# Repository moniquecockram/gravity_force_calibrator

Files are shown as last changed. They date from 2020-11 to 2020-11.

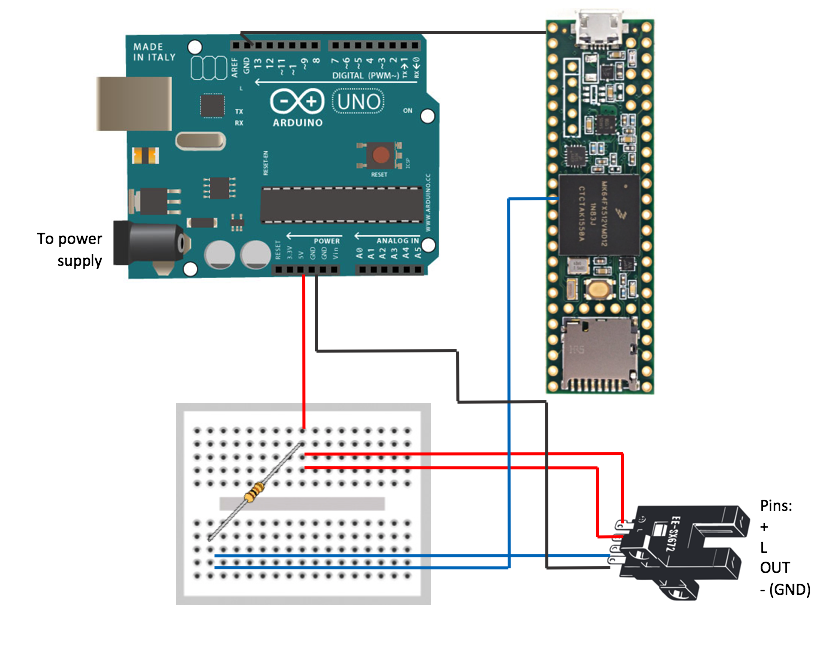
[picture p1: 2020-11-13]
Part Images/wiring_diagram.png

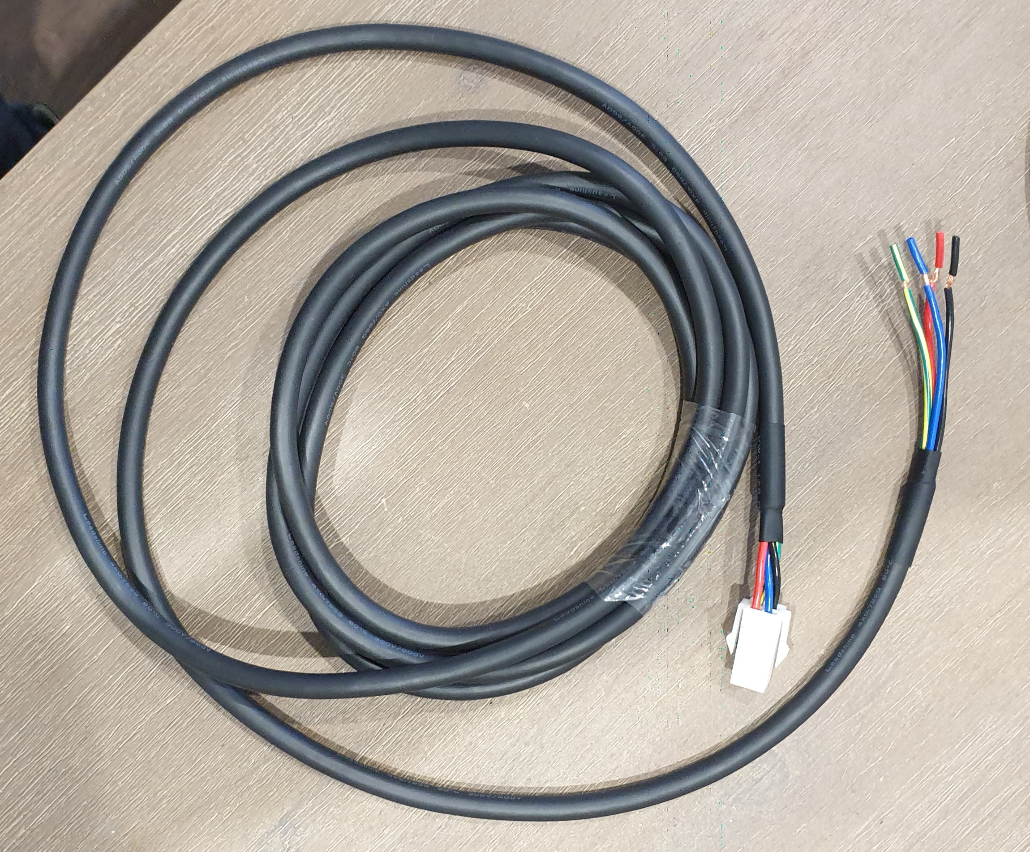
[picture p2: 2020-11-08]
Part Images/Metre Power Extension Cable for Easy Servo Motors_1.jpg

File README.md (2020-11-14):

# gravity_force_calibrator
A wheely good project.

The current version of the code to run the prototype is in folder control_code. 

The simple code for reading photogate data is in photogate_MArk1.

Other useful information on the various aspects of the project are in other folders as labelled.

Ryan Husband and Monique Cockram

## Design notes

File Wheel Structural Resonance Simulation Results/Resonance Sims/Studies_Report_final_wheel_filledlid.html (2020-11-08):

Image Width (pixels):

# Study Report

Analyzed File | better_combined_filledlid v9
Version | Autodesk Fusion 360 (2.0.8809)
Creation Date | 2020-08-21, 23:20:54
Author | ryanh

#### Project Properties

Title | Studies
Author | ryanh

## Simulation Model 1:1

### Study 1 - Modal Frequencies

##### Study Properties

Study Type | Modal Frequencies
Last Modification Date | 2020-08-21, 21:56:54

#### Settings

##### General

Contact Tolerance | 0.1 mm
Number of Modes | 10
Frequency Range [Hz] | No
Compute Preloaded Modes | Yes
Enhanced Accuracy | No

##### Damping

##### Mesh

Average Element Size (% of model size)
Solids | 3
Scale Mesh Size Per Part | No
Average Element Size (absolute value) | -
Element Order | Parabolic
Create Curved Mesh Elements | Yes
Max. Turn Angle on Curves (Deg.) | 60
Max. Adjacent Mesh Size Ratio | 1.5
Max. Aspect Ratio | 10
Minimum Element Size (% of average size) | 20

##### Adaptive Mesh Refinement

Number of Refinement Steps | 0
Results Convergence Tolerance (%) | 20
Frequency Mode | 1

#### Materials

Component | Material | Safety Factor
Body1 | Aluminum | Yield Strength
Body3 | Aluminum | Yield Strength
better_combined_innerlid v13:1 | Aluminum | Yield Strength
better_combined_innerlid v13:1/weight_lids v2:1 | Aluminum | Yield Strength
better_combined_innerlid v13:1/weight_lids v2:2 | Aluminum | Yield Strength
better_combined_innerlid v13:1/better_combined v19:1/axel v5:1 | Aluminum | Yield Strength
better_combined_innerlid v13:1/better_combined v19:1/design_MArk2 v17:1 | Aluminum | Yield Strength
better_combined_innerlid v13:1/better_combined v19:1/weights v2:1 | Steel | Yield Strength
better_combined_innerlid v13:1/better_combined v19:1/weights v2:2 | Steel | Yield Strength
better_combined_innerlid v13:1/better_combined v19:1/holders v12:1 | Aluminum | Yield Strength
better_combined_innerlid v13:1/better_combined v19:1/holders v12:2 | Aluminum | Yield Strength

##### Aluminum

Density | 2.7E-06 kg / mm^3
Young's Modulus | 68900 MPa
Poisson's Ratio | 0.33
Yield Strength | 275 MPa
Ultimate Tensile Strength | 310 MPa
Thermal Conductivity | 0.23 W / (mm C)
Thermal Expansion Coefficient | 2.36E-05 / C
Specific Heat | 897 J / (kg C)

##### Steel

Density | 7.85E-06 kg / mm^3
Young's Modulus | 210000 MPa
Poisson's Ratio | 0.3
Yield Strength | 207 MPa
Ultimate Tensile Strength | 345 MPa
Thermal Conductivity | 0.056 W / (mm C)
Thermal Expansion Coefficient | 1.2E-05 / C
Specific Heat | 480 J / (kg C)

#### Contacts

##### Bonded

Name

[S] Bonded1 [weights v2:2||holders v12:2]

[S] Bonded2 [weights v2:1||holders v12:1]

[S] Bonded3 [design_MArk2 v17:1||weights v2:1]

[S] Bonded4 [design_MArk2 v17:1||holders v12:1]

[S] Bonded5 [design_MArk2 v17:1||holders v12:1]

[S] Bonded6 [design_MArk2 v17:1||holders v12:1]

[S] Bonded7 [design_MArk2 v17:1||weights v2:1]

[S] Bonded8 [design_MArk2 v17:1||weights v2:1]

[S] Bonded9 [design_MArk2 v17:1||weights v2:2]

[S] Bonded10 [design_MArk2 v17:1||holders v12:2]

[S] Bonded11 [design_MArk2 v17:1||holders v12:2]

[S] Bonded12 [design_MArk2 v17:1||weights v2:2]

[S] Bonded13 [design_MArk2 v17:1||weights v2:2]

[S] Bonded14 [design_MArk2 v17:1||holders v12:1]

[S] Bonded15 [design_MArk2 v17:1||holders v12:1]

[S] Bonded16 [design_MArk2 v17:1||weights v2:1]

[S] Bonded17 [design_MArk2 v17:1||holders v12:2]

[S] Bonded18 [design_MArk2 v17:1||holders v12:2]

[S] Bonded19 [design_MArk2 v17:1||weights v2:2]

[S] Bonded20 [design_MArk2 v17:1||weights v2:1]

[S] Bonded21 [design_MArk2 v17:1||holders v12:2]

[S] Bonded22 [design_MArk2 v17:1||weights v2:2]

[S] Bonded23 [axel v5:1||design_MArk2 v17:1]

[S] Bonded24 [weight_lids v2:2||holders v12:1]

[S] Bonded25 [weight_lids v2:2||weights v2:1]

[S] Bonded26 [weight_lids v2:2||design_MArk2 v17:1]

[S] Bonded27 [weight_lids v2:1||holders v12:2]

[S] Bonded28 [weight_lids v2:1||weights v2:2]

[S] Bonded29 [weight_lids v2:1||design_MArk2 v17:1]

[S] Bonded30 [better_combined_innerlid v13:1||weight_lids v2:2]

[S] Bonded31 [better_combined_innerlid v13:1||weight_lids v2:1]

[S] Bonded32 [better_combined_innerlid v13:1||design_MArk2 v17:1]

[S] Bonded33 [better_combined_innerlid v13:1||design_MArk2 v17:1]

[S] Bonded34 [better_combined_innerlid v13:1||design_MArk2 v17:1]

[S] Bonded35 [better_combined_innerlid v13:1||design_MArk2 v17:1]

[S] Bonded36 [better_combined_innerlid v13:1||design_MArk2 v17:1]

[S] Bonded37 [better_combined_innerlid v13:1||design_MArk2 v17:1]

[S] Bonded38 [better_combined_innerlid v13:1||design_MArk2 v17:1]

[S] Bonded39 [better_combined_innerlid v13:1||design_MArk2 v17:1]

[S] Bonded40 [better_combined_innerlid v13:1||weights v2:1]

[S] Bonded41 [better_combined_innerlid v13:1||holders v12:1]

[S] Bonded42 [better_combined_innerlid v13:1||holders v12:1]

[S] Bonded43 [better_combined_innerlid v13:1||holders v12:1]

[S] Bonded44 [better_combined_innerlid v13:1||weights v2:1]

[S] Bonded45 [better_combined_innerlid v13:1||weights v2:1]

[S] Bonded46 [better_combined_innerlid v13:1||weights v2:2]

[S] Bonded47 [better_combined_innerlid v13:1||holders v12:2]

[S] Bonded48 [better_combined_innerlid v13:1||holders v12:2]

[S] Bonded49 [better_combined_innerlid v13:1||weights v2:2]

[S] Bonded50 [better_combined_innerlid v13:1||weights v2:2]

[S] Bonded51 [better_combined_innerlid v13:1||holders v12:1]

[S] Bonded52 [better_combined_innerlid v13:1||holders v12:1]

[S] Bonded53 [better_combined_innerlid v13:1||weights v2:1]

[S] Bonded54 [better_combined_innerlid v13:1||holders v12:2]

[S] Bonded55 [better_combined_innerlid v13:1||holders v12:2]

[S] Bonded56 [better_combined_innerlid v13:1||weights v2:2]

[S] Bonded57 [better_combined_innerlid v13:1||weights v2:1]

[S] Bonded58 [better_combined_innerlid v13:1||holders v12:2]

[S] Bonded59 [better_combined_innerlid v13:1||weights v2:2]

[S] Bonded60 [better_combined_innerlid v13:1||axel v5:1]

[S] Bonded61 [Simulation Model 1:1(Body3)||design_MArk2 v17:1]

[S] Bonded62 [Simulation Model 1:1(Body3)||better_combined_innerlid v13:1]

[S] Bonded63 [Simulation Model 1:1(Body3)||better_combined_innerlid v13:1]

[S] Bonded64 [Simulation Model 1:1(Body3)||design_MArk2 v17:1]

[S] Bonded65 [Simulation Model 1:1(Body3)||better_combined_innerlid v13:1]

[S] Bonded66 [Simulation Model 1:1(Body3)||better_combined_innerlid v13:1]

[S] Bonded67 [Simulation Model 1:1(Body1)||design_MArk2 v17:1]

[S] Bonded68 [Simulation Model 1:1(Body1)||better_combined_innerlid v13:1]

[S] Bonded69 [Simulation Model 1:1(Body1)||better_combined_innerlid v13:1]

[S] Bonded70 [Simulation Model 1:1(Body1)||design_MArk2 v17:1]

[S] Bonded71 [Simulation Model 1:1(Body1)||better_combined_innerlid v13:1]

[S] Bonded72 [Simulation Model 1:1(Body1)||better_combined_innerlid v13:1]

#### Mesh

Type | Nodes | Elements
Solids | 476671 | 314592

#### Load Case1

#### Constraints

##### Frictionless1

Type | Frictionless

###### Selected Entities

For correct interpretation of this image use e.g. IE9, Chrome, Safari, Firefox

##### Pin1

Type | Pin
Radial | Yes
Axial | Yes
Tangential | No

###### Selected Entities

For correct interpretation of this image use e.g. IE9, Chrome, Safari, Firefox

##### Pin2

Type | Pin
Radial | Yes
Axial | Yes
Tangential | No

###### Selected Entities

For correct interpretation of this image use e.g. IE9, Chrome, Safari, Firefox

#### Loads

##### Gravity

Type | Gravity
Magnitude | 9.807 m / s^2
X Value | 0 m / s^2
Y Value | 0 m / s^2
Z Value | -9.807 m / s^2

###### Selected Entities

For correct interpretation of this image use e.g. IE9, Chrome, Safari, Firefox

##### Angular Global Load1

Type | Angular Global Load
Velocity
Magnitude | 360 deg / s
X Value | 0 deg / s
Y Value | 0 deg / s
Z Value | -360 deg / s
X Distance | 0 mm
Y Distance | 0 mm
Z Distance | 0 mm

###### Selected Entities

For correct interpretation of this image use e.g. IE9, Chrome, Safari, Firefox

#### Results

##### Result Summary

Frequency | Participation X | Participation Y | Participation Z
Mode 1: 117.6 Hz | 0 | 0 | 0
Mode 2: 1059 Hz | 0.0015 | 0 | 0
Mode 3: 1109 Hz | 0 | 0.0002 | 0
Mode 4: 1588 Hz | 0 | 0 | 84.2124999
Mode 5: 2258 Hz | 0 | 0.0002 | 1.19500002
Mode 6: 2334 Hz | 0 | 0 | 0.0005
Mode 7: 2814 Hz | 0.0012 | 89.0425026 | 0
Mode 8: 3084 Hz | 89.5721018 | 0.001 | 0
Mode 9: 4229 Hz | 0 | 0.0005 | 0.0003
Mode 10: 4243 Hz | 0 | 0 | 0.239500008

##### Total Modal Displacement

###### Mode 1: 117.6 Hz Total Modal Displacement

0 1

For correct interpretation of this image use e.g. IE9, Chrome, Safari, Firefox

###### Mode 2: 1059 Hz Total Modal Displacement

0 1

For correct interpretation of this image use e.g. IE9, Chrome, Safari, Firefox

###### Mode 3: 1109 Hz Total Modal Displacement

0 1

For correct interpretation of this image use e.g. IE9, Chrome, Safari, Firefox

###### Mode 4: 1588 Hz Total Modal Displacement

0 1

For correct interpretation of this image use e.g. IE9, Chrome, Safari, Firefox

###### Mode 5: 2258 Hz Total Modal Displacement

0 1

For correct interpretation of this image use e.g. IE9, Chrome, Safari, Firefox

###### Mode 6: 2334 Hz Total Modal Displacement

0 1

For correct interpretation of this image use e.g. IE9, Chrome, Safari, Firefox

###### Mode 7: 2814 Hz Total Modal Displacement

0 1

For correct interpretation of this image use e.g. IE9, Chrome, Safari, Firefox

###### Mode 8: 3084 Hz Total Modal Displacement

0 1

For correct interpretation of this image use e.g. IE9, Chrome, Safari, Firefox

###### Mode 9: 4229 Hz Total Modal Displacement

0 1

For correct interpretation of this image use e.g. IE9, Chrome, Safari, Firefox

###### Mode 10: 4243 Hz Total Modal Displacement

0 1

For correct interpretation of this image use e.g. IE9, Chrome, Safari, Firefox

Image Width (pixels):

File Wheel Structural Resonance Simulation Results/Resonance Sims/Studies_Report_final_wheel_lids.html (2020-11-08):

Image Width (pixels):

# Study Report

Analyzed File | better_combined_outerlids v5
Version | Autodesk Fusion 360 (2.0.8809)
Creation Date | 2020-08-21, 18:55:14
Author | ryanh

#### Project Properties

Title | Studies
Author | ryanh

## Simulation Model 1:1

### Study 1 - Modal Frequencies

##### Study Properties

Study Type | Modal Frequencies
Last Modification Date | 2020-08-21, 17:08:25

#### Settings

##### General

Contact Tolerance | 0.1 mm
Number of Modes | 10
Frequency Range [Hz] | No
Compute Preloaded Modes | Yes
Enhanced Accuracy | No

##### Damping

##### Mesh

Average Element Size (% of model size)
Solids | 3
Scale Mesh Size Per Part | No
Average Element Size (absolute value) | -
Element Order | Parabolic
Create Curved Mesh Elements | Yes
Max. Turn Angle on Curves (Deg.) | 60
Max. Adjacent Mesh Size Ratio | 1.5
Max. Aspect Ratio | 10
Minimum Element Size (% of average size) | 20

##### Adaptive Mesh Refinement

Number of Refinement Steps | 0
Results Convergence Tolerance (%) | 20
Frequency Mode | 1

#### Materials

Component | Material | Safety Factor
better_combined v17:1/axel v5:1 | Aluminum | Yield Strength
better_combined v17:1/design_MArk2 v17:1 | Aluminum | Yield Strength
better_combined v17:1/weights v2:1 | Steel | Yield Strength
better_combined v17:1/weights v2:2 | Steel | Yield Strength
better_combined v17:1/holders v12:1 | Aluminum | Yield Strength
better_combined v17:1/holders v12:2 | Aluminum | Yield Strength
lid v4:1 | Aluminum | Yield Strength
lid v4:2 | Aluminum | Yield Strength

##### Aluminum

Density | 2.7E-06 kg / mm^3
Young's Modulus | 68900 MPa
Poisson's Ratio | 0.33
Yield Strength | 275 MPa
Ultimate Tensile Strength | 310 MPa
Thermal Conductivity | 0.23 W / (mm C)
Thermal Expansion Coefficient | 2.36E-05 / C
Specific Heat | 897 J / (kg C)

##### Steel

Density | 7.85E-06 kg / mm^3
Young's Modulus | 210000 MPa
Poisson's Ratio | 0.3
Yield Strength | 207 MPa
Ultimate Tensile Strength | 345 MPa
Thermal Conductivity | 0.056 W / (mm C)
Thermal Expansion Coefficient | 1.2E-05 / C
Specific Heat | 480 J / (kg C)

#### Contacts

##### Bonded

Name

[M] [S] Bonded1 [lid v4:1||design_MArk2 v17:1]

[M] [S] Bonded2 [lid v4:2||design_MArk2 v17:1]

[M] [S] Bonded3 [weights v2:1||design_MArk2 v17:1]

[M] [S] Bonded4 [weights v2:2||design_MArk2 v17:1]

[M] [S] Bonded5 [holders v12:2||design_MArk2 v17:1]

[M] [S] Bonded6 [holders v12:1||design_MArk2 v17:1]

[M] [S] Bonded7 [lid v4:1||axel v5:1]

[M] [S] Bonded8 [lid v4:2||axel v5:1]

[S] Bonded9 [holders v12:2||lid v4:1]

[S] Bonded10 [holders v12:1||lid v4:1]

[S] Bonded11 [weights v2:2||lid v4:1]

[S] Bonded12 [weights v2:2||holders v12:2]

[S] Bonded13 [weights v2:1||lid v4:1]

[S] Bonded14 [weights v2:1||holders v12:1]

[S] Bonded15 [design_MArk2 v17:1||weights v2:1]

[S] Bonded16 [design_MArk2 v17:1||holders v12:1]

[S] Bonded17 [design_MArk2 v17:1||holders v12:1]

[S] Bonded18 [design_MArk2 v17:1||weights v2:1]

[S] Bonded19 [design_MArk2 v17:1||weights v2:1]

[S] Bonded20 [design_MArk2 v17:1||weights v2:2]

[S] Bonded21 [design_MArk2 v17:1||holders v12:2]

[S] Bonded22 [design_MArk2 v17:1||holders v12:2]

[S] Bonded23 [design_MArk2 v17:1||weights v2:2]

[S] Bonded24 [design_MArk2 v17:1||weights v2:2]

[S] Bonded25 [design_MArk2 v17:1||holders v12:1]

[S] Bonded26 [design_MArk2 v17:1||holders v12:1]

[S] Bonded27 [design_MArk2 v17:1||holders v12:2]

[S] Bonded28 [design_MArk2 v17:1||holders v12:2]

[S] Bonded29 [design_MArk2 v17:1||weights v2:1]

[S] Bonded30 [design_MArk2 v17:1||weights v2:2]

[S] Bonded31 [axel v5:1||design_MArk2 v17:1]

#### Mesh

Type | Nodes | Elements
Solids | 655869 | 426144

#### Load Case1

#### Constraints

##### Frictionless1

Type | Frictionless

###### Selected Entities

For correct interpretation of this image use e.g. IE9, Chrome, Safari, Firefox

##### Pin1

Type | Pin
Radial | Yes
Axial | Yes
Tangential | No

###### Selected Entities

For correct interpretation of this image use e.g. IE9, Chrome, Safari, Firefox

##### Pin2

Type | Pin
Radial | Yes
Axial | Yes
Tangential | No

###### Selected Entities

For correct interpretation of this image use e.g. IE9, Chrome, Safari, Firefox

##### Pin3

Type | Pin
Radial | Yes
Axial | Yes
Tangential | No

###### Selected Entities

For correct interpretation of this image use e.g. IE9, Chrome, Safari, Firefox

##### Pin4

Type | Pin
Radial | Yes
Axial | Yes
Tangential | No

###### Selected Entities

For correct interpretation of this image use e.g. IE9, Chrome, Safari, Firefox

#### Loads

##### Gravity

Type | Gravity
Magnitude | 9.807 m / s^2
X Value | 0 m / s^2
Y Value | 0 m / s^2
Z Value | -9.807 m / s^2

###### Selected Entities

For correct interpretation of this image use e.g. IE9, Chrome, Safari, Firefox

##### Angular Global Load1

Type | Angular Global Load
Velocity
Magnitude | 360 deg / s
X Value | 0 deg / s
Y Value | 0 deg / s
Z Value | -360 deg / s
X Distance | 0 mm
Y Distance | 0 mm
Z Distance | 0 mm

###### Selected Entities

For correct interpretation of this image use e.g. IE9, Chrome, Safari, Firefox

#### Results

##### Result Summary

Frequency | Participation X | Participation Y | Participation Z
Mode 1: 61.13 Hz | 0 | 0 | 0
Mode 2: 827.1 Hz | 0 | 0.0065 | 0.0001
Mode 3: 1020 Hz | 0.0043 | 0 | 0.022
Mode 4: 1078 Hz | 0 | 0 | 75.8481026
Mode 5: 1839 Hz | 0 | 84.751302 | 0
Mode 6: 1979 Hz | 0 | 0.0002 | 3.38249989
Mode 7: 2213 Hz | 0 | 0.033099999 | 0
Mode 8: 2217 Hz | 0.0001 | 0.620900001 | 0
Mode 9: 2257 Hz | 0 | 0.0017 | 0.0003
Mode 10: 2311 Hz | 0 | 0 | 1.02129998

##### Total Modal Displacement

###### Mode 1: 61.13 Hz Total Modal Displacement

0.001 1

For correct interpretation of this image use e.g. IE9, Chrome, Safari, Firefox

###### Mode 2: 827.1 Hz Total Modal Displacement

0 1

For correct interpretation of this image use e.g. IE9, Chrome, Safari, Firefox

###### Mode 3: 1020 Hz Total Modal Displacement

0 1

For correct interpretation of this image use e.g. IE9, Chrome, Safari, Firefox

###### Mode 4: 1078 Hz Total Modal Displacement

0 1

For correct interpretation of this image use e.g. IE9, Chrome, Safari, Firefox

###### Mode 5: 1839 Hz Total Modal Displacement

0 1

For correct interpretation of this image use e.g. IE9, Chrome, Safari, Firefox

###### Mode 6: 1979 Hz Total Modal Displacement

0 1

For correct interpretation of this image use e.g. IE9, Chrome, Safari, Firefox

###### Mode 7: 2213 Hz Total Modal Displacement

0 1

For correct interpretation of this image use e.g. IE9, Chrome, Safari, Firefox

###### Mode 8: 2217 Hz Total Modal Displacement

0 1

For correct interpretation of this image use e.g. IE9, Chrome, Safari, Firefox

###### Mode 9: 2257 Hz Total Modal Displacement

0 1

For correct interpretation of this image use e.g. IE9, Chrome, Safari, Firefox

###### Mode 10: 2311 Hz Total Modal Displacement

0 1

For correct interpretation of this image use e.g. IE9, Chrome, Safari, Firefox

Image Width (pixels):

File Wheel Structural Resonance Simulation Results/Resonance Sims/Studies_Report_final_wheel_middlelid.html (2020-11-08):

Image Width (pixels):

# Study Report

Analyzed File | better_combined_innerlid v11
Version | Autodesk Fusion 360 (2.0.8809)
Creation Date | 2020-08-21, 21:32:29
Author | ryanh

#### Project Properties

Title | Studies
Author | ryanh

## Simulation Model 1:1

### Study 1 - Modal Frequencies

##### Study Properties

Study Type | Modal Frequencies
Last Modification Date | 2020-08-21, 21:18:28

#### Settings

##### General

Contact Tolerance | 0.1 mm
Number of Modes | 10
Frequency Range [Hz] | No
Compute Preloaded Modes | Yes
Enhanced Accuracy | No

##### Damping

##### Mesh

Average Element Size (% of model size)
Solids | 3
Scale Mesh Size Per Part | No
Average Element Size (absolute value) | -
Element Order | Parabolic
Create Curved Mesh Elements | Yes
Max. Turn Angle on Curves (Deg.) | 60
Max. Adjacent Mesh Size Ratio | 1.5
Max. Aspect Ratio | 10
Minimum Element Size (% of average size) | 20

##### Adaptive Mesh Refinement

Number of Refinement Steps | 0
Results Convergence Tolerance (%) | 20
Frequency Mode | 1

#### Materials

Component | Material | Safety Factor
Body1 | Aluminum | Yield Strength
better_combined v18:1/axel v5:1 | Aluminum | Yield Strength
better_combined v18:1/design_MArk2 v17:1 | Aluminum | Yield Strength
better_combined v18:1/weights v2:1 | Steel | Yield Strength
better_combined v18:1/weights v2:2 | Steel | Yield Strength
better_combined v18:1/holders v12:1 | Aluminum | Yield Strength
better_combined v18:1/holders v12:2 | Aluminum | Yield Strength
weight_lids v2:1 | Aluminum | Yield Strength
weight_lids v2:2 | Aluminum | Yield Strength

##### Aluminum

Density | 2.7E-06 kg / mm^3
Young's Modulus | 68900 MPa
Poisson's Ratio | 0.33
Yield Strength | 275 MPa
Ultimate Tensile Strength | 310 MPa
Thermal Conductivity | 0.23 W / (mm C)
Thermal Expansion Coefficient | 2.36E-05 / C
Specific Heat | 897 J / (kg C)

##### Steel

Density | 7.85E-06 kg / mm^3
Young's Modulus | 210000 MPa
Poisson's Ratio | 0.3
Yield Strength | 207 MPa
Ultimate Tensile Strength | 345 MPa
Thermal Conductivity | 0.056 W / (mm C)
Thermal Expansion Coefficient | 1.2E-05 / C
Specific Heat | 480 J / (kg C)

#### Contacts

##### Bonded

Name

[M] [S] Bonded3 [Simulation Model 1:1||]

[M] [S] Bonded4 [||Simulation Model 1:1]

[M] [S] Bonded6 [||Simulation Model 1:1]

[M] [S] Bonded7 [||Simulation Model 1:1]

[S] Bonded61 [holders v12:2||weight_lids v2:1]

[S] Bonded62 [holders v12:1||weight_lids v2:2]

[S] Bonded63 [weights v2:2||weight_lids v2:1]

[S] Bonded64 [weights v2:2||holders v12:2]

[S] Bonded65 [weights v2:1||weight_lids v2:2]

[S] Bonded66 [weights v2:1||holders v12:1]

[S] Bonded67 [design_MArk2 v17:1||weight_lids v2:2]

[S] Bonded68 [design_MArk2 v17:1||weight_lids v2:1]

[S] Bonded69 [design_MArk2 v17:1||weights v2:1]

[S] Bonded70 [design_MArk2 v17:1||holders v12:1]

[S] Bonded71 [design_MArk2 v17:1||holders v12:1]

[S] Bonded72 [design_MArk2 v17:1||holders v12:1]

[S] Bonded73 [design_MArk2 v17:1||weights v2:1]

[S] Bonded74 [design_MArk2 v17:1||weights v2:1]

[S] Bonded75 [design_MArk2 v17:1||weights v2:2]

[S] Bonded76 [design_MArk2 v17:1||holders v12:2]

[S] Bonded77 [design_MArk2 v17:1||holders v12:2]

[S] Bonded78 [design_MArk2 v17:1||weights v2:2]

[S] Bonded79 [design_MArk2 v17:1||weights v2:2]

[S] Bonded80 [design_MArk2 v17:1||holders v12:1]

[S] Bonded81 [design_MArk2 v17:1||holders v12:1]

[S] Bonded82 [design_MArk2 v17:1||weights v2:1]

[S] Bonded83 [design_MArk2 v17:1||holders v12:2]

[S] Bonded84 [design_MArk2 v17:1||holders v12:2]

[S] Bonded85 [design_MArk2 v17:1||weights v2:2]

[S] Bonded86 [design_MArk2 v17:1||weights v2:1]

[S] Bonded87 [design_MArk2 v17:1||holders v12:2]

[S] Bonded88 [design_MArk2 v17:1||weights v2:2]

[S] Bonded89 [axel v5:1||design_MArk2 v17:1]

[S] Bonded90 [Simulation Model 1:1||weight_lids v2:2]

[S] Bonded91 [Simulation Model 1:1||weight_lids v2:1]

[S] Bonded92 [Simulation Model 1:1||design_MArk2 v17:1]

[S] Bonded93 [Simulation Model 1:1||design_MArk2 v17:1]

[S] Bonded94 [Simulation Model 1:1||design_MArk2 v17:1]

[S] Bonded95 [Simulation Model 1:1||design_MArk2 v17:1]

[S] Bonded96 [Simulation Model 1:1||design_MArk2 v17:1]

[S] Bonded97 [Simulation Model 1:1||design_MArk2 v17:1]

[S] Bonded98 [Simulation Model 1:1||design_MArk2 v17:1]

[S] Bonded99 [Simulation Model 1:1||design_MArk2 v17:1]

[S] Bonded100 [Simulation Model 1:1||weights v2:1]

[S] Bonded101 [Simulation Model 1:1||holders v12:1]

[S] Bonded102 [Simulation Model 1:1||holders v12:1]

[S] Bonded103 [Simulation Model 1:1||holders v12:1]

[S] Bonded104 [Simulation Model 1:1||weights v2:1]

[S] Bonded105 [Simulation Model 1:1||weights v2:1]

[S] Bonded106 [Simulation Model 1:1||weights v2:2]

[S] Bonded107 [Simulation Model 1:1||holders v12:2]

[S] Bonded108 [Simulation Model 1:1||holders v12:2]

[S] Bonded109 [Simulation Model 1:1||weights v2:2]

[S] Bonded110 [Simulation Model 1:1||weights v2:2]

[S] Bonded111 [Simulation Model 1:1||holders v12:1]

[S] Bonded112 [Simulation Model 1:1||holders v12:1]

[S] Bonded113 [Simulation Model 1:1||weights v2:1]

[S] Bonded114 [Simulation Model 1:1||holders v12:2]

[S] Bonded115 [Simulation Model 1:1||holders v12:2]

[S] Bonded116 [Simulation Model 1:1||weights v2:2]

[S] Bonded117 [Simulation Model 1:1||weights v2:1]

[S] Bonded118 [Simulation Model 1:1||holders v12:2]

[S] Bonded119 [Simulation Model 1:1||weights v2:2]

[S] Bonded120 [Simulation Model 1:1||axel v5:1]

#### Mesh

Type | Nodes | Elements
Solids | 215918 | 136483

#### Load Case1

#### Constraints

##### Frictionless1

Type | Frictionless

###### Selected Entities

For correct interpretation of this image use e.g. IE9, Chrome, Safari, Firefox

##### Pin1

Type | Pin
Radial | Yes
Axial | Yes
Tangential | No

###### Selected Entities

For correct interpretation of this image use e.g. IE9, Chrome, Safari, Firefox

##### Pin2

Type | Pin
Radial | Yes
Axial | Yes
Tangential | No

###### Selected Entities

For correct interpretation of this image use e.g. IE9, Chrome, Safari, Firefox

#### Loads

##### Gravity

Type | Gravity
Magnitude | 9.807 m / s^2
X Value | 0 m / s^2
Y Value | 0 m / s^2
Z Value | -9.807 m / s^2

###### Selected Entities

For correct interpretation of this image use e.g. IE9, Chrome, Safari, Firefox

##### Angular Global Load1

Type | Angular Global Load
Velocity
Magnitude | 360 deg / s
X Value | 0 deg / s
Y Value | 0 deg / s
Z Value | -360 deg / s
X Distance | 0 mm
Y Distance | 0 mm
Z Distance | 0 mm

###### Selected Entities

For correct interpretation of this image use e.g. IE9, Chrome, Safari, Firefox

#### Results

##### Result Summary

Frequency | Participation X | Participation Y | Participation Z
Mode 1: 132.3 Hz | 0 | 0 | 0
Mode 2: 645 Hz | 0 | 0.0021 | 0
Mode 3: 935.3 Hz | 0 | 0 | 61.7972016
Mode 4: 1024 Hz | 0.0073 | 0 | 0.0005
Mode 5: 1151 Hz | 0 | 0.0088 | 0.0004
Mode 6: 1153 Hz | 0 | 0.0001 | 0.039199999
Mode 7: 1227 Hz | 16.2856996 | 0 | 0
Mode 8: 1256 Hz | 0.0005 | 0 | 0
Mode 9: 1486 Hz | 0 | 65.9582019 | 0
Mode 10: 1513 Hz | 0 | 0 | 15.5499995

##### Total Modal Displacement

###### Mode 1: 132.3 Hz Total Modal Displacement

0 1

For correct interpretation of this image use e.g. IE9, Chrome, Safari, Firefox

###### Mode 2: 645 Hz Total Modal Displacement

0 1

For correct interpretation of this image use e.g. IE9, Chrome, Safari, Firefox

###### Mode 3: 935.3 Hz Total Modal Displacement

0 1

For correct interpretation of this image use e.g. IE9, Chrome, Safari, Firefox

###### Mode 4: 1024 Hz Total Modal Displacement

0 1

For correct interpretation of this image use e.g. IE9, Chrome, Safari, Firefox

###### Mode 5: 1151 Hz Total Modal Displacement

0 1

For correct interpretation of this image use e.g. IE9, Chrome, Safari, Firefox

###### Mode 6: 1153 Hz Total Modal Displacement

0 1

For correct interpretation of this image use e.g. IE9, Chrome, Safari, Firefox

###### Mode 7: 1227 Hz Total Modal Displacement

0 1

For correct interpretation of this image use e.g. IE9, Chrome, Safari, Firefox

###### Mode 8: 1256 Hz Total Modal Displacement

0 1

For correct interpretation of this image use e.g. IE9, Chrome, Safari, Firefox

###### Mode 9: 1486 Hz Total Modal Displacement

0 1

For correct interpretation of this image use e.g. IE9, Chrome, Safari, Firefox

###### Mode 10: 1513 Hz Total Modal Displacement

0 1

For correct interpretation of this image use e.g. IE9, Chrome, Safari, Firefox

Image Width (pixels):

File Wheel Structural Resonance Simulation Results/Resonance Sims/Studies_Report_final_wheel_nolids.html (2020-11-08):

Image Width (pixels):

# Study Report

Analyzed File | better_combined v17
Version | Autodesk Fusion 360 (2.0.8809)
Creation Date | 2020-08-21, 16:36:01
Author | ryanh

#### Project Properties

Title | Studies
Author | ryanh

## Simulation Model 1:1

### Study 1 - Modal Frequencies

##### Study Properties

Study Type | Modal Frequencies
Last Modification Date | 2020-08-21, 16:21:24

#### Settings

##### General

Contact Tolerance | 0.1 mm
Number of Modes | 10
Frequency Range [Hz] | No
Compute Preloaded Modes | Yes
Enhanced Accuracy | No

##### Damping

##### Mesh

Average Element Size (% of model size)
Solids | 3
Scale Mesh Size Per Part | No
Average Element Size (absolute value) | -
Element Order | Parabolic
Create Curved Mesh Elements | Yes
Max. Turn Angle on Curves (Deg.) | 60
Max. Adjacent Mesh Size Ratio | 1.5
Max. Aspect Ratio | 10
Minimum Element Size (% of average size) | 20

##### Adaptive Mesh Refinement

Number of Refinement Steps | 0
Results Convergence Tolerance (%) | 20
Frequency Mode | 1

#### Materials

Component | Material | Safety Factor
design_MArk2 v17:1 | Aluminum | Yield Strength
axel v5:1 | Aluminum | Yield Strength
weights v2:1 | Steel | Yield Strength
weights v2:2 | Steel | Yield Strength
holders v12:1 | Aluminum | Yield Strength
holders v12:3 | Aluminum | Yield Strength

##### Aluminum

Density | 2.7E-06 kg / mm^3
Young's Modulus | 68900 MPa
Poisson's Ratio | 0.33
Yield Strength | 275 MPa
Ultimate Tensile Strength | 310 MPa
Thermal Conductivity | 0.23 W / (mm C)
Thermal Expansion Coefficient | 2.36E-05 / C
Specific Heat | 897 J / (kg C)

##### Steel

Density | 7.85E-06 kg / mm^3
Young's Modulus | 210000 MPa
Poisson's Ratio | 0.3
Yield Strength | 207 MPa
Ultimate Tensile Strength | 345 MPa
Thermal Conductivity | 0.056 W / (mm C)
Thermal Expansion Coefficient | 1.2E-05 / C
Specific Heat | 480 J / (kg C)

#### Contacts

##### Bonded

Name

[M] [S] Bonded2 [weights v2:2||design_MArk2 v17:1]

[M] [S] Bonded3 [design_MArk2 v17:1||weights v2:1]

[M] [S] Bonded4 [design_MArk2 v17:1||holders v12:1]

[M] [S] Bonded5 [design_MArk2 v17:1||holders v12:3]

[M] [S] Bonded6 [design_MArk2 v17:1||axel v5:1]

[S] Bonded7 [weights v2:2||holders v12:3]

[S] Bonded8 [weights v2:1||holders v12:1]

[S] Bonded9 [design_MArk2 v17:1||weights v2:1]

[S] Bonded10 [design_MArk2 v17:1||holders v12:1]

[S] Bonded11 [design_MArk2 v17:1||holders v12:1]

[S] Bonded12 [design_MArk2 v17:1||weights v2:1]

[S] Bonded13 [design_MArk2 v17:1||weights v2:1]

[S] Bonded14 [design_MArk2 v17:1||weights v2:2]

[S] Bonded15 [design_MArk2 v17:1||holders v12:3]

[S] Bonded16 [design_MArk2 v17:1||holders v12:3]

[S] Bonded17 [design_MArk2 v17:1||weights v2:2]

[S] Bonded18 [design_MArk2 v17:1||weights v2:2]

[S] Bonded19 [design_MArk2 v17:1||holders v12:1]

[S] Bonded20 [design_MArk2 v17:1||holders v12:1]

[S] Bonded21 [design_MArk2 v17:1||holders v12:3]

[S] Bonded22 [design_MArk2 v17:1||holders v12:3]

[S] Bonded23 [design_MArk2 v17:1||weights v2:1]

[S] Bonded24 [design_MArk2 v17:1||weights v2:2]

#### Mesh

Type | Nodes | Elements
Solids | 70580 | 44054

#### Load Case1

#### Constraints

##### Pin2

Type | Pin
Radial | Yes
Axial | Yes
Tangential | No

###### Selected Entities

For correct interpretation of this image use e.g. IE9, Chrome, Safari, Firefox

##### Pin3

Type | Pin
Radial | Yes
Axial | Yes
Tangential | No

###### Selected Entities

For correct interpretation of this image use e.g. IE9, Chrome, Safari, Firefox

##### Frictionless2

Type | Frictionless

###### Selected Entities

For correct interpretation of this image use e.g. IE9, Chrome, Safari, Firefox

#### Loads

##### Gravity

Type | Gravity
Magnitude | 9.807 m / s^2
X Value | 0 m / s^2
Y Value | 0 m / s^2
Z Value | -9.807 m / s^2

###### Selected Entities

For correct interpretation of this image use e.g. IE9, Chrome, Safari, Firefox

##### Angular Global Load2

Type | Angular Global Load
Velocity
Magnitude | 360 deg / s
X Value | 0 deg / s
Y Value | 0 deg / s
Z Value | -360 deg / s
X Distance | 0 mm
Y Distance | 0 mm
Z Distance | 0 mm

###### Selected Entities

For correct interpretation of this image use e.g. IE9, Chrome, Safari, Firefox

#### Results

##### Result Summary

Frequency | Participation X | Participation Y | Participation Z
Mode 1: 162.1 Hz | 0 | 0 | 0
Mode 2: 666.4 Hz | 0 | 0.0014 | 0
Mode 3: 909.3 Hz | 0 | 71.3082016 | 0.0067
Mode 4: 919.5 Hz | 0 | 0.0071 | 66.3258016
Mode 5: 942 Hz | 0.0077 | 0.0001 | 0.0124
Mode 6: 1212 Hz | 28.1147003 | 0.0001 | 0
Mode 7: 1249 Hz | 0.0012 | 0 | 0
Mode 8: 1397 Hz | 0 | 0 | 12.9108995
Mode 9: 1595 Hz | 0 | 0 | 0.0044
Mode 10: 2170 Hz | 0 | 0 | 0.0003

##### Total Modal Displacement

###### Mode 1: 162.1 Hz Total Modal Displacement

0 1

For correct interpretation of this image use e.g. IE9, Chrome, Safari, Firefox

###### Mode 2: 666.4 Hz Total Modal Displacement

0 1

For correct interpretation of this image use e.g. IE9, Chrome, Safari, Firefox

###### Mode 3: 909.3 Hz Total Modal Displacement

0 1

For correct interpretation of this image use e.g. IE9, Chrome, Safari, Firefox

###### Mode 4: 919.5 Hz Total Modal Displacement

0 1

For correct interpretation of this image use e.g. IE9, Chrome, Safari, Firefox

###### Mode 5: 942 Hz Total Modal Displacement

0 1

For correct interpretation of this image use e.g. IE9, Chrome, Safari, Firefox

###### Mode 6: 1212 Hz Total Modal Displacement

0 1

For correct interpretation of this image use e.g. IE9, Chrome, Safari, Firefox

###### Mode 7: 1249 Hz Total Modal Displacement

0 1

For correct interpretation of this image use e.g. IE9, Chrome, Safari, Firefox

###### Mode 8: 1397 Hz Total Modal Displacement

0 1

For correct interpretation of this image use e.g. IE9, Chrome, Safari, Firefox

###### Mode 9: 1595 Hz Total Modal Displacement

0 1

For correct interpretation of this image use e.g. IE9, Chrome, Safari, Firefox

###### Mode 10: 2170 Hz Total Modal Displacement

0 1

For correct interpretation of this image use e.g. IE9, Chrome, Safari, Firefox

Image Width (pixels):

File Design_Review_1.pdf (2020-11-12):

# PHYS6701 Design Report 1

### Monique Cockram and Ryan Husband

### August 2020

## 1 Executive Summary

TorPeDO is a Torsion Pendulum Dual Oscillator designed to measure gravitational tidal forces. To assist in deriving meaning from TorPeDO’s measurements, a wheel of rotating masses has been devised to generate a calibration signal for TorPeDO. The following document reviews the design of a Newtonian force calibrator for TorPeDO. This review includes an analysis of the project’s purpose to extend TorPeDO’s function, the calibrator’s design as a weighted wheel simulating Newtonian forces induced by rotating point masses, the wheel’s rotation mechanism by a DC servomotor, timing belt and Hall sensor for speed control as well as details of the project requirements, timeline and work breakdown. The prototype is still in the design stage at the time of release of this report, but the ideas demonstrated are the solid foundations of what is looking to be a successful project.

## 2 Introduction

The Center of Gravitational Physics (OzGrav) at the Australian National University uses a range of devices sensitive to gravitational tidal forces to conduct experiments. These gravity sensitive devices are constantly under the influence of gravitational disturbances from sources such as local traffic and the moon, invoking uncertainty in experimental data. To mitigate these external gravitational influence on experiments, OzGrav constructed a Torsion Pendulum Dual Oscillator (TorPeDO), as depicted in Figure 1. TorPeDO can accurately measure gravitational tidal forces, such that the local gravity over the time each experiment is conducted can be recorded and used in the analysis of the experiment’s result to uncover any influence from unwanted gravitational sources.

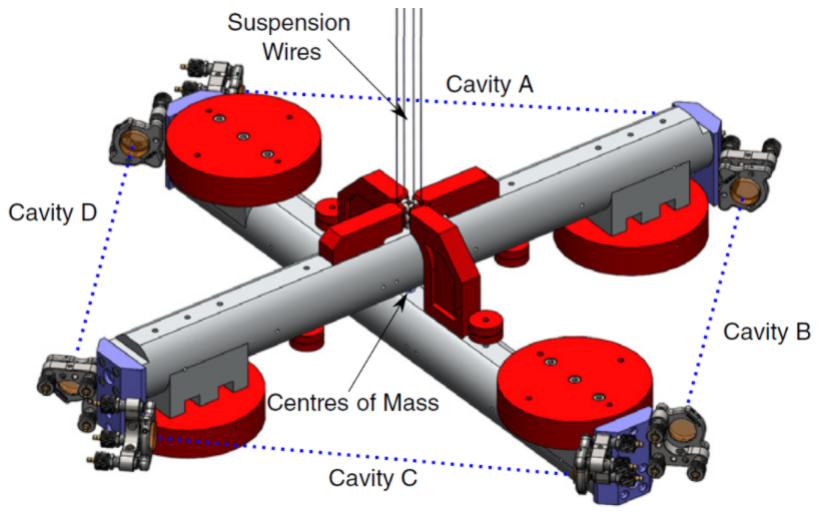
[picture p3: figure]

Figure 1: Schematic of TorPeDO, where the red cylinders are dense masses simulating point masses in free space [1].

Like any successful measuring instrument, TorPeDO requires a measurement standard to derive meaning from its data [2]. In its current form, TorPeDO relies on past measurement data for a relative comparison to derive inference from current data. A better inference method for TorPeDO would utilise a well defined baseline signal for universal comparison from each measurement TorPeDO conducts. The purpose of this project is to develop a prototype device to generate this reference signal for TorPeDO’s measurements; a Newtonian force calibrator.

## 3 Technical Design Details

### 3.1 Overall Design

TorPeDO consists of two suspended crossbeams which are free to rotate about the same axis in the same plane (i.e. the suspension wires and the plane of each cavity as seen in Figure 1). Gravitational tidal forces accelerate the end masses on each arm of TorPeDO, inducing an differential rotation between TorPeDO’s arms which is measured by the change in each Fabry-Perot cavity length [1]. The ideal calibration signal for a device reliant on oscillations for measurement would consist of a single frequency; a sinusoid [2][3]. Similar calibration prototypes constructed at the advanced LIGO detector suggest the best mechanism for inducing a sinusoidal gravitational signal is a wheel of fixed rotating masses [4]. The wheel prototyped at LIGO, depicted in Figure 2, was thus the basis for the design of TorPeDO’s Newtonian force calibrator.

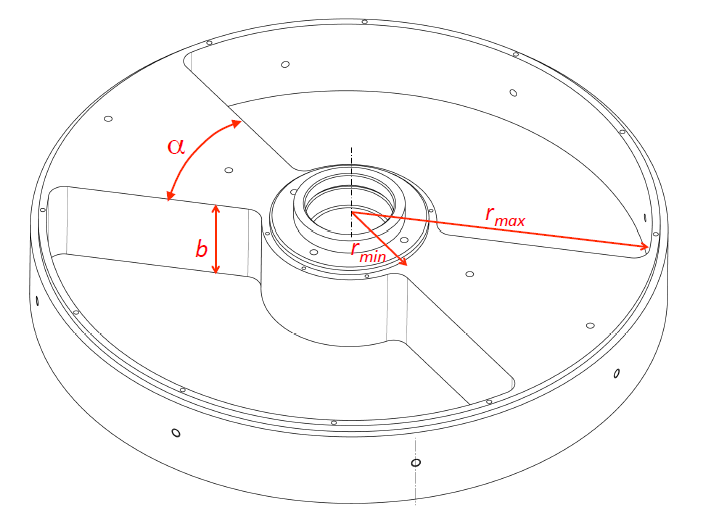
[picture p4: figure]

Figure 2: Schematic of Newtonian force calibrator prototype used on the advanced LIGO detector, constructed from aluminium [4].

The prototype of Figure 2 was used on LIGO’s mirrors to infer a sinusoidal calibration signal in LIGO’s interferometry measurements. This wheel was unique in that it simulated the effect of rotating masses on LIGO’s measurements, allowing for ease of calibration as the gravitational force induced by the wheel on LIGO was well defined and simple to calculate.

### 3.2 Specific Components

### 3.2.1 The Wheel Design

The Newtonian force calibrator for TorPeDO was therefore going be an echo and improvement on the design of Figure 2. These improvements include:

- Replicating Newtonian force generated by point masses. LIGO’s prototype utilised infilled sectors of a ring as their masses as seen in Figure 2, where these masses were approximated as ‘point-like’ resulting in a range of approximate affects on LIGO [4]. TorPeDO’s calibration device would therefore use smaller volume masses of a higher density material to improve on these approximations;
- Using heavier masses to produce a stronger gravitation signal as the gravitational force between bodies is linearly proportional to their masses. LIGO’s prototype masses were approximately 2.06kg each where as TorPeDO’s calibrator masses are planned to be approximately 5kg each; and
- Allowing the masses to be replaceable, allow flexibility in generation of specific calibration signal.

Implementing these improvements upon LIGO’s prototype and making some further adjustments, the first design of TorPeDO’s Newtonian force calibrator was developed as shown in Figure 3.

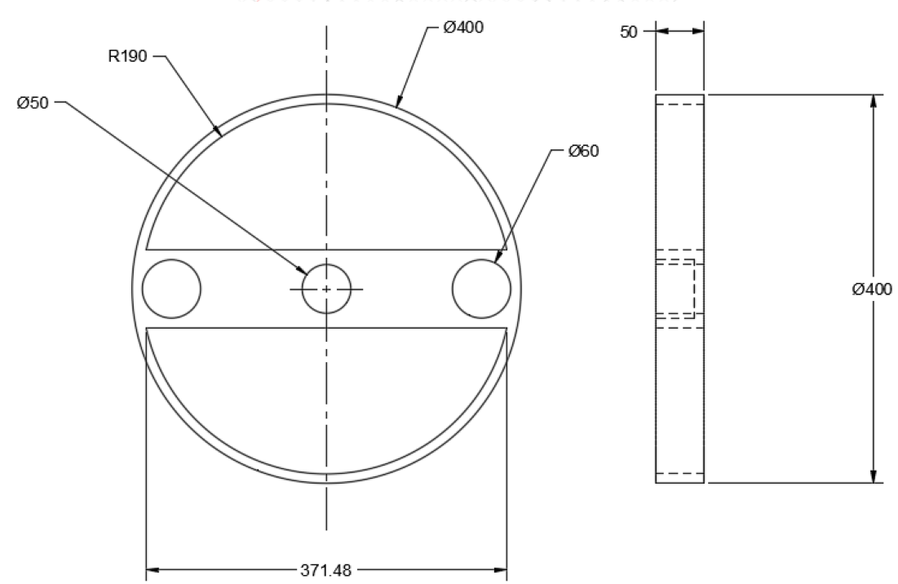
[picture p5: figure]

Figure 3: First Newtonian force calibrator design for TorPeDO. Note that the dimensions shown are approximations as this is a proof of concept design.

The wheel body demonstrated in Figure 3 is constructed of aluminium as this is the most light weight, sturdy and available metal. The wheel consists of placeholder holes for the weights, to be constructed of steel as this is a readily available metal of higher density than aluminium. The body also echo’s the ring design of LIGO’s prototype wheel [4] and consists of an axle hole at its center.

### 3.2.2 The Rotation Mechanism

The key aspects of the rotation mechanism fit together as seen in Figure 4. The key features include a timing belt, which is used to reduce resonances and minimise slippage and gyrations, both of which are important for smooth and stable rotations.

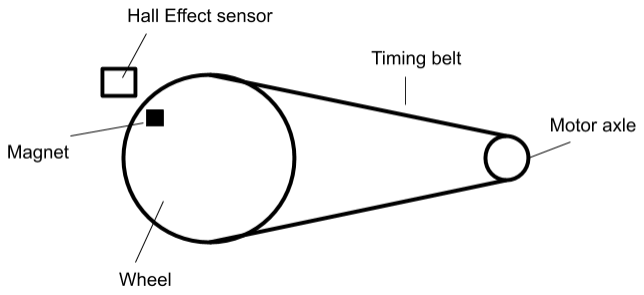
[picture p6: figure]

Figure 4: A rough diagram of the components of the mechanism of rotation.

The motor will be a DC servomotor, as these have the most precise speed and position control out of all the options under consideration. In addition, the client suggested a 24V motor as the best choice, and there will be a need to get significant power sources in order to rotate the mass of the wheel. From a quick calculation using our current estimations of dimensions of the wheel, the amount of torque the motor could need is about 18Nm, which is achievable with many of the motors available. In terms of the rotation speed measurement, we will use a

Hall Effect sensor to monitor and control the speed of the motor using a feedback loop, which will be in the computer control system that will be developed. This will be done using either an Arduino or Raspberry Pi, depending on what best fits the final choice of motor and sensor. As a result, a sensor with digital output will be best for this application. This feedback loop will take the current speed of the wheel and try and minimise its difference compared to the chosen speed of rotation. The output signal will therefore be proportional to the change in the motor needed to maintain a constant rotation speed. A possible improvement to Figure 4 is to use multiple magnets and Hall Effect sensors around the circumference of the wheel in order to maximise the accuracy thought frequent monitoring of the speed. This will ensure the rotation is as constant as is achievable for this project, and thus optimising the gravity force signal that TorPeDO reads and is calibrated with.

## 4 Requirements Review

The most important and overarching client requirement is to maximise the stability of the Newtonian force calibrator. This will be achieved in a number of ways, but with the current design in particular the timing belt will assist in achieving this. The design of the wheel will also be made as balanced and symmetrical as possible in order to minimise gyrations.
The calibrator also needs to be of a reasonable size to work within the allocated lab space around TorPeDO. In response to this, this initial wheel design from Figure 3 is 40cm in diameter, allowing plenty of leeway to move around in the spaces that are at a minimum about 50cm wide. Pending further discussions and refinements, this can be easily changed in future versions of the design.
Additionally, there needs to be accurate measurement and control of the rotation speed in order to obtain the desired gravity signal from the calibrator. By using multiple Hall Effect sensors around the circumference of the wheel, this will be be maximised for this version of the project.
Other specifications from the client included a rotation speed of 1 − 10Hz, which will be implemented and tested once construction has commenced. In addition, the rotating masses were suggested to be greater than 1kg, thus two 5kg masses were chosen in order to be a significant size as compared with that of TorPeDO, which uses has 3kg masses on each are as seen in Figure 1.

## 5 Revised Timeline

Figure 5 outlines the ideal progression of this project as it stands currently. It is expected that the duration of each of the tasks will vary, however following this will assist the project

in reaching completion.

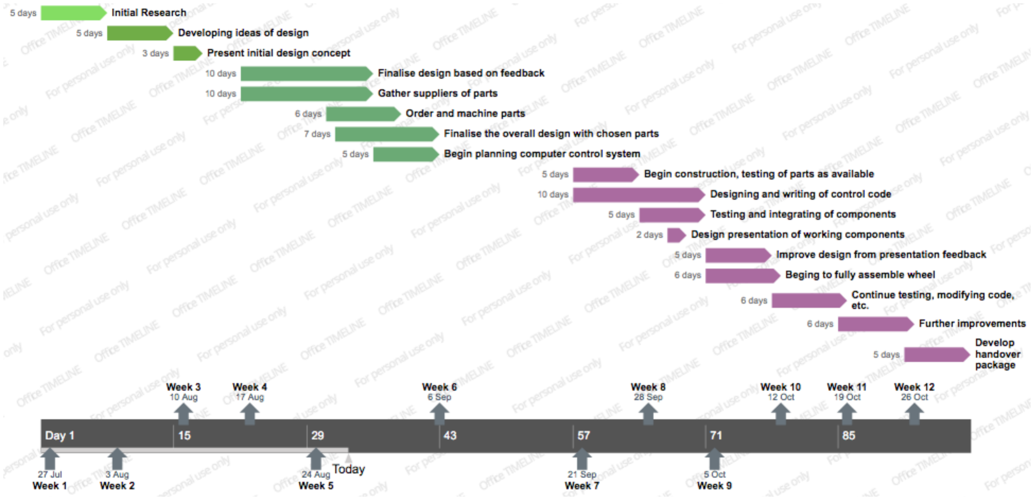
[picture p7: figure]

Figure 5: An outline of the current proposed timeline for the project.

### 5.1 Work Breakdown

At the current progression of this project, the work has been split into design of the wheel and the design of the rotation mechanism such that these tasks have been divided up on a per person basis. This may change for future work however, as the periods of time when the wheel is being machined and ordered parts are being delivered may result in both team persons working on the same part of the project simultaneously. Examples of the tasks where this could be done include programming the computer control of the wheel with the Arduino or Raspberri Pi or simulating the measurement data TorPeDO will generate once the wheel is constructed and ready for testing to verify its performance.

## 6 Conclusion

At present, a draft design of the rotation mechanism and wheel construction for a Newtonian force calibrator has been produced. The wheel is an echo of the Newtonian force calibrator prototype developed by LIGO as well as an improvement in properties including the use of more appropriately shaped, weighted and interchangeable ‘point-like’ masses. The rotation mechanics will utilise a DC servomotor attached to a timing belt wrapped about the wheel’s axle. The rotation speed will be monitored with a Hall effect sensor which will produce an error feedback signal to the motor for accurate rotation control. This document also reviewed the client’s requirements, revised the timeline of project goals and discussed the past and future breakdowns of work between group members.

## References

[1] D. J. McManus, “Dual torsion pendulum sensor for measurement of terrestrial gravitational forces,” PhD thesis, The Australian National University, Canberra, ACT, Jun. 2019.
[2] M. Lombardi, “An introduction to frequency calibration - part i,” Cal Lab: International Journal of Metrology, vol. 3, pp. 17–28, Jan. 1996.
[3] MAtthew D. Schwartz, Matthew d. schwartz lectures on oscillator analysis, http://users.physics.harvard.edu/˜schwartz/15cFiles/15c-2015-Schwartz.pdf, (http://users.physics.harvard.edu/~schwartz/15cFiles/15c-2015-Schwartz.pdf) 2015.
[4] D. Estevez, B. Lieunard, F. Marion, B. Mours, L. Rolland, and D. Verkindt, “First tests of a newtonian calibrator on an interferometric gravitational wave detector,” Jun. 2018.

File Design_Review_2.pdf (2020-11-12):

# PHYS6701 Design Report 2

### Monique Cockram and Ryan Husband

### September 2020

## 1 Executive Summary

This document outlines the final design of the first iteration of a Newtonian Force Calibrator for the TorPeDO system. An introduction on the purpose of such a product is provided, before the details of the design is discussed. In particular, the wheel design is justified, a description of the rotation mechanism’s use of pulleys and timing belts is provided, and the securing structure for the whole calibrator is outlined. The client’s requirements for this project are also revisited, as well as an update on the budget, timeline, and work breakdown. This design review also outlines the next stages of this project of construction and testing.

## 2 Introduction

The Center of Gravitational Physics (OzGrav) at the Australian National University uses a range of devices sensitive to gravitational tidal forces to conduct experiments. These gravity sensitive devices are constantly under the influence of gravitational disturbances from sources such as local traffic and the moon, invoking uncertainty in experimental data. To mitigate these external gravitational influence on experiments, OzGrav constructed a Torsion Pendulum Dual Oscillator (TorPeDO), as depicted in Figure 1. TorPeDO can accurately measure gravitational tidal forces, such that the local gravity over the time each experiment is conducted can be recorded and used in the analysis of the experiment’s result to uncover any influence from unwanted gravitational sources.

Like any successful measuring instrument, TorPeDO requires a measurement standard to derive meaning from its data [1]. In its current form, TorPeDO relies on past measurement data for a relative comparison to derive inference from current data. A better inference method for TorPeDO would utilise a well defined baseline signal for universal comparison from each measurement TorPeDO conducts. The purpose of this project is to develop a prototype device to generate this reference signal for TorPeDO’s measurements; a Newtonian force calibrator (NCal).

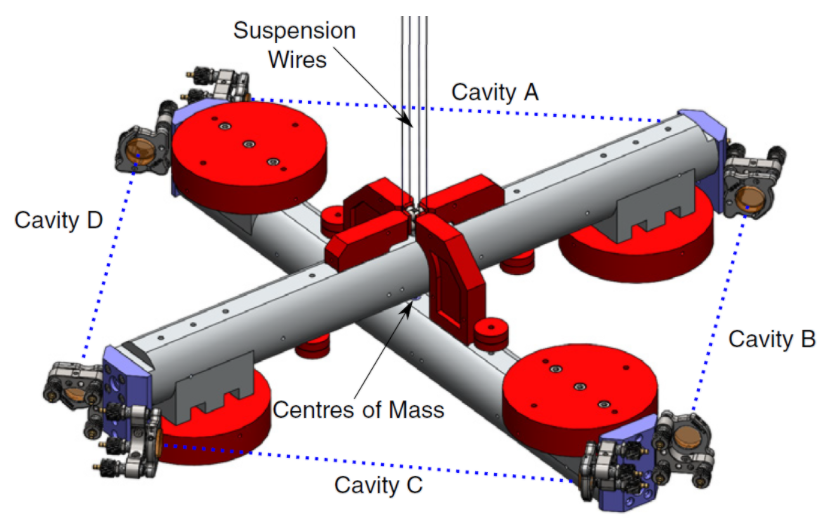
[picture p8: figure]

Figure 1: Schematic of TorPeDO, where the red cylinders are dense masses simulating point masses in free space [2].

The initial design review of this project consisted of preliminary compositions for the rotation mechanism and wheel construction. This initial review focused on the wheel as an echo of the Newtonian force calibrator prototype developed by LIGO[3], where the initial design is demonstrated in Figure 2. The key improvements on this wheel architecture compared to that of LIGO included the use of more appropriately shaped, weighted and interchangeable ‘point-like’ masses. Another key focus of the initial review was the rotation mechanics and their utilisation of a DC servomotor attached to a timing belt wrapped about the wheel’s axle. The rotation speed would be monitored with a Hall effect sensor which would produce an error feedback signal to the motor for accurate rotation control. The client’s requirements, revised the timeline of project goals and discussions of the past and future breakdowns of work between group members was also covered.
This document addresses the changes made and additions to the initial TorPeDO NCal prototype design as well as reflecting the current state of the project and required future work.

## 3 Technical Design Details

The physical design of the NCal prototype is a growth of the idea presented in Figure 2. Not only does the design consist of the wheel and rotation mechanisms themselves, but also an axle, a means of attaching the axle to the wheel, an outer casing for the wheel and masses, a means to hold the wheel in place along a fixed rotating axis within said casing and an improved system for speed measurement.

### 3.1 Specific Components

### 3.1.1 The Wheel and Mass Positioning Architecture

The wheel’s new design consists of a more realistic approach to the desired theoretical model for making the NCal signal, alongside features to implement other components of the prototype. The initial and final designs for the wheel body are demonstrated in Figure 2.

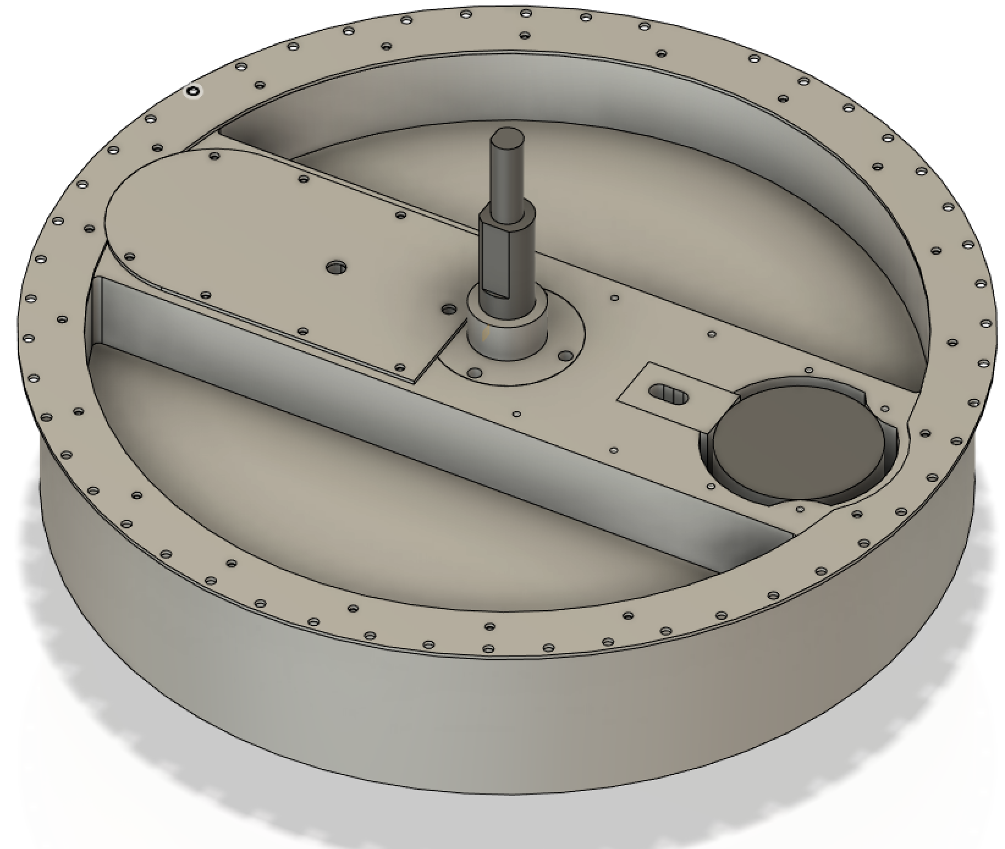
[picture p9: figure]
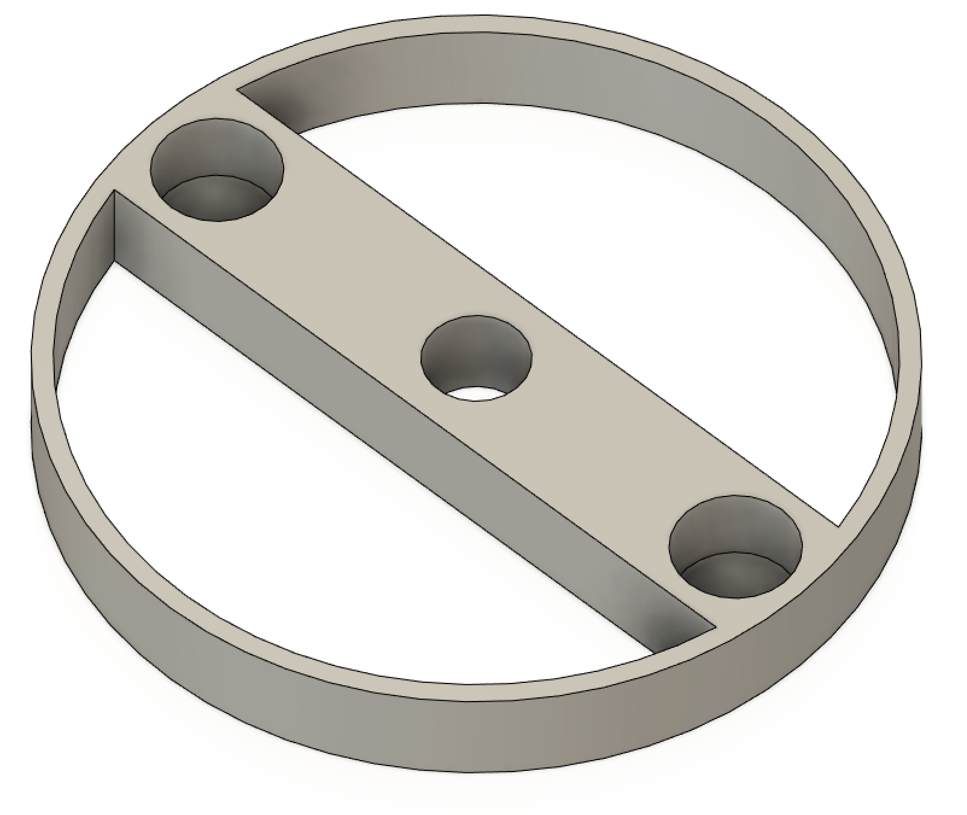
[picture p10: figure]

Figure 2: The initial (left) and final (right) designs of the wheel. Note the final design also demonstrates the axle attachment with the collar, as well as the mass positioning mechanism and chopper wheel attachment. There is also only one weight lid showing to demonstrate their purpose.

As discussed in the initial design report, the initial design of the wheel body was based upon the design of LIGO’s wheel [3]. The updates applied to develop the current wheel shown in Figure 2 include:

- Implementing a three-point contact mechanism for the masses. Another prototype of LIGO’s NCal consisted of weight holes [4] as echoed in the initial NCal design for TorPeDO. To secure the masses in this manner however, LIGO had to heat the holes on their wheel such that they would expand and contract around the masses when inserted. To ease the method of adding weights to the wheel, a three-point stability mechanism was used instead as shown in Figure 2. The weights would first be inserted into the hole, after which a smaller slanted weight holder piece would be inserted into the wheel against the weight, acting as the third point of contact between the wheel and weight. This would also allow adjustment of the weight positions such that they can be located exactly 30cm apart as desired;
- Increasing the wheel’s diameter from 400mm to 420mm. This was required to make room for the larger hole sizes for the three-point weight positioning system.
- Increasing the wheel’s thickness to 90mm and changing the weight’s masses to 3kg. these changes were required to keep the wheel’s size within the client’s requirements and to keep the overall prototype at a reasonable weight;
- Adding the appropriate screw holes for the axle, weight lid and chopper wheel attachment mechanisms. A collar is applied over the axle to fit tightly into a socket onto the wheel where the angle between the axle and wheel plane can be adjusted to as close to 90◦ as possible to minimise gyration. The chopper wheel is applied to the wheel body for speed measurement via the photogate. Furthermore, the weight lids are added to ensure the masses are both vertically and horizontally secure within the wheel’s body; and

- Applying an infill material layer to the wheel in the gaps between the bows and the center frame. This was implemented as a result of the project supervisor highlighting a concern with potential structural resonances on the bows from the rotational motion. A series of simulations were conducted to determine the best wheel design that would keep the structural resonances as far from the rotational frequency as possible. A 10mm infill in the center plane of the wheel was found to be the most appropriate wheel architecture.

### 3.1.2 The Securing Structure, Base Plate and Outer Casing

With the wheel’s design set, a mechanism to hold the wheel in place was required. To do this, a base plate and securing structure components were developed as demonstrated in Figure 3, a design inspired by that used by LIGO’s NCal prototype [4]. Both the base plate and securing structure consist of 25mm thick aluminium. Each component of the securing structure is separated into blocks to simplify machining. The center of both the base place and securing structure lid consist of four M12 screw holes where flange bearings will be placed. These flange bearings will attach to either end of the wheel’s axle to fix its rotation axis in space as shown in Figure 4. The other screw holes on the securing structure lid consist of six M8 screws to attach to the walls and a number of M6 screws to mount the motor to the structure. The base plate utilises the three-point contact mechanism from the wheel’s architecture to ensure the entire NCal will sit flat on a surface when used to ensure the wheel rotates in the horizontal plane. The base plate is attached to the securing structure via six M8 screws, and consists of an additional twenty M6 screw holes for application of an outer casing demonstrated in Figure 5.

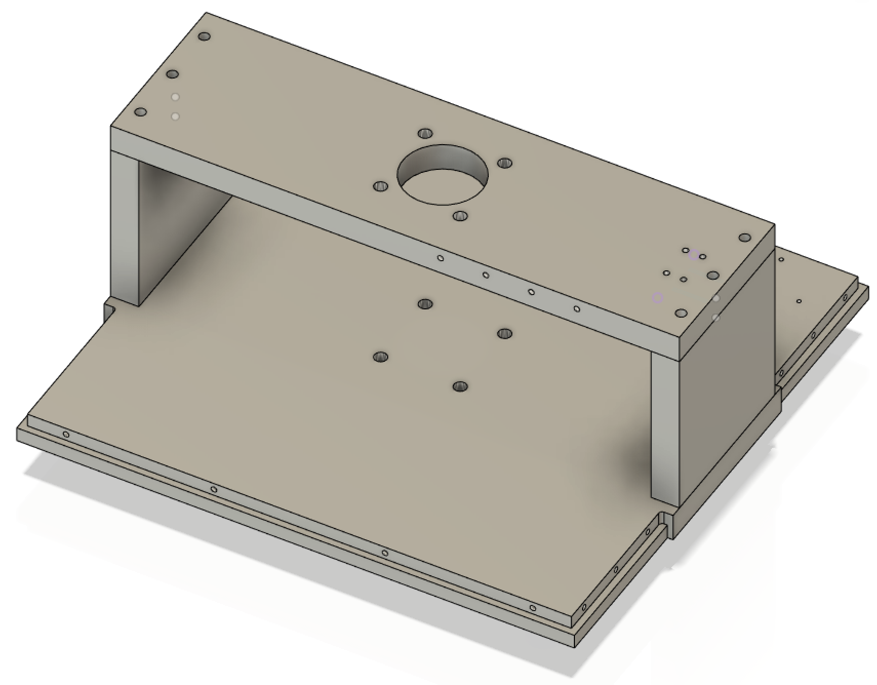
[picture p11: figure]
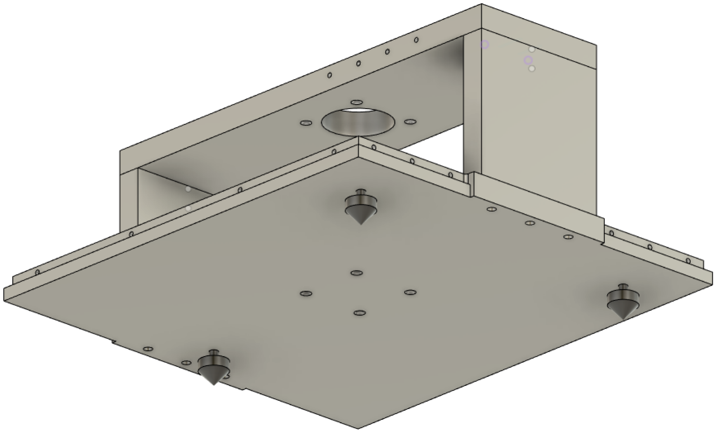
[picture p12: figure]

Figure 3: The securing structure and base plate prototype designs.

### 3.1.3 The Rotation Mechanism and Speed Control

The key aspects of the rotation mechanism fit together as seen in Figure 4, and specific part numbers are found in Table 1. The key features include a timing belt, which is used to reduce resonances and minimise slippage and gyrations, both of which are important for smooth and stable rotations. A belt width of 16mm was chosen for a combination of strength and stability, and the availability of pulleys that fit the other requirements of this design. Additionally, pulleys (not shown in Figure 4) of slightly different diameters (63.85mm and 47.95mm) will be added to the top of the wheel and motor axles respectively, to further reduce resonances from amplification by their respective rotations and to simplify future changes to the rotation mechanism should they be required.

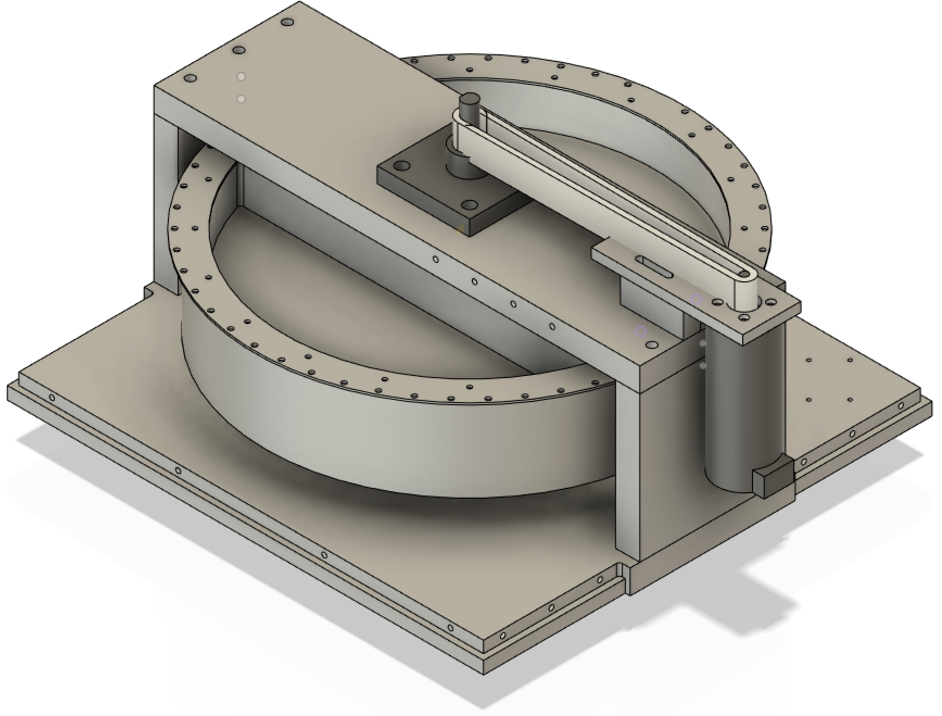
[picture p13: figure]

Figure 4: The wheel secured to the outer structure via the axle and flange bearings, fixed in the plane of rotation.

The motor used is a 180W DC servomotor as seen in Figure 4, as these have the most precise speed and position control out of all the options under consideration. The motor mount consists of a 10mm aluminium plate with slotted holes, attached to the securing structure lid through a spacer plate. The 10mm thick aluminium plate uses this thickness to reduce motor vibrations on the timing belt. The slotted holes of the motor mount and spacer plate are required to add horizontal tension to the timing belt and ensure the wheel and motor axles are aligned vertically respectively. The chosen motor also has a built in encoder, which can be used for monitoring of the rotation speed of the wheel.
Another means of monitoring the rotation speed comes in the form of a photogate, as seen implemented in the prototype in Figure 5. The photogate will be implemented to control the speed of the motor using a feedback loop, which will be in the computer control system under development. The computer control system consists of a Teensy 3.5 microprocessor development board, which will use the signal from the photogate due to the integrated optical chopper wheel as seen in Figure 4 and 2, to determine the rotation speed of the wheel. This will ensure the rotation is as constant as possible, thus optimising the stability of the NCal signal induced upon TorPeDO.

### 3.1.4 Overall Design

The assembled components of the NCal prototype are demonstrated in Figure 5. Notably, the outer casing applied to each side of the exposed wheel. The outer casing is constructed from 6mm thick aluminium plates held together by M4 screws and is required for safety reasons as a heavy spinning wheel can be dangerous if care is not taken around the device. Furthermore, the photogate is applied to the roof of one of the outer casings. The roof for this outer casing in particular consists of a square slotted hole, such that the photogate can be attached to a small aluminium plate, situated on the slotted hole and slid into place such that the optical axis of the photogate is secured over the holes of the chopper wheel.

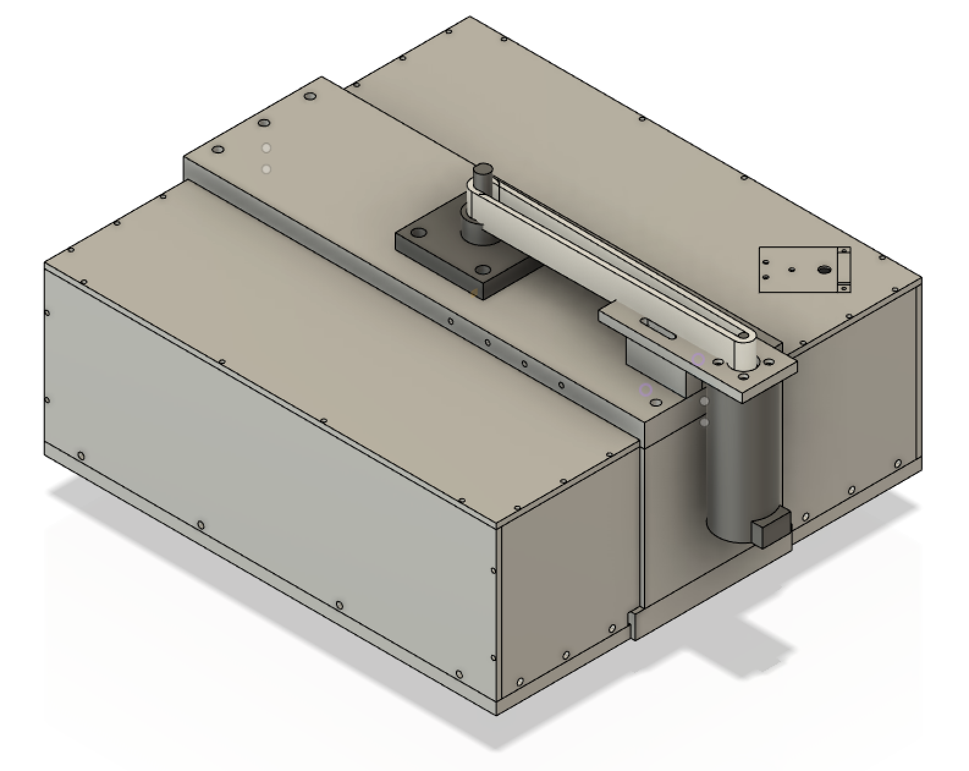
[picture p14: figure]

Figure 5: The final NCal prototype design for TorPeDO, with outer casing and photogate applied.

## 4 Requirements Review

The most important and overarching client requirement is to maximise the stability of the Newtonian force calibrator. This will be achieved in a number of ways, but with the current design in particular the timing belt will assist in achieving this. The design of the wheel will also be made as balanced and symmetrical as possible in order to minimise gyrations.
The calibrator also needs to be of a reasonable size to work within the allocated lab space around TorPeDO. In response to this, this initial wheel design from Figure 3 is 40cm in diameter, allowing plenty of leeway to move around in the spaces that are at a minimum about 50cm wide. Pending further discussions and refinements, this can be easily changed in future versions of the design.
Additionally, there needs to be accurate measurement and control of the rotation speed in order to obtain the desired gravity signal from the calibrator. By using a chopper wheel with 49 holes around the circumference of the wheel, this large number of measurements made by the photogate in a single rotation will thus maximise the accuracy of measurements.

Safety is also an important requirement from the client, so the development of a strong casing in this design is a key factor. In addition, the three-point contact mechanism on the base plate increases stability thus safety of the calibrator.
Other specifications from the client included a rotation speed of 1 − 10Hz, which will be implemented in the control code and tested once construction has commenced. In addition, the rotating masses were suggested to be greater than 1kg, thus two 3kg masses were chosen in this version of the design. This was reduced from the 5kg of the previous design review, as the total mass of the wheel needed to be reduced for greater ease of transportation.

## 5 Revised Budget and Timeline

### 5.1 Budget

For the current iteration of the design, the components needed to be purchased have been finalised, excluding the machining of the wheel mechanism, so current total spending can be outlined in Table 1.

Component | Supplier | Item Code | Cost ($)
Servomotor Kit | Ocean Controls | CNC-116 | 654.50
Teensy 3.5 Board | Core Electronics | DEV-14055 | 54.04
Bearings x2 | RS Components | 750-8775 | 17.51 ea
Timing Belt | RS Components | 474-6277 | 44.64
Pulley | RS Components | 745-725 | 34.43
Pulley | RS Components | 745-719 | 32.81
Photogate | RS Components | 219-2296 | 52.97
| | Total | 908.41

Table 1: Outline of the current spending of the project.

### 5.2 Timeline

Figure 6 outlines the ideal progression of this project as it stands currently. It is expected that the duration of each of the tasks will vary, however following this will assist the project in reaching completion.

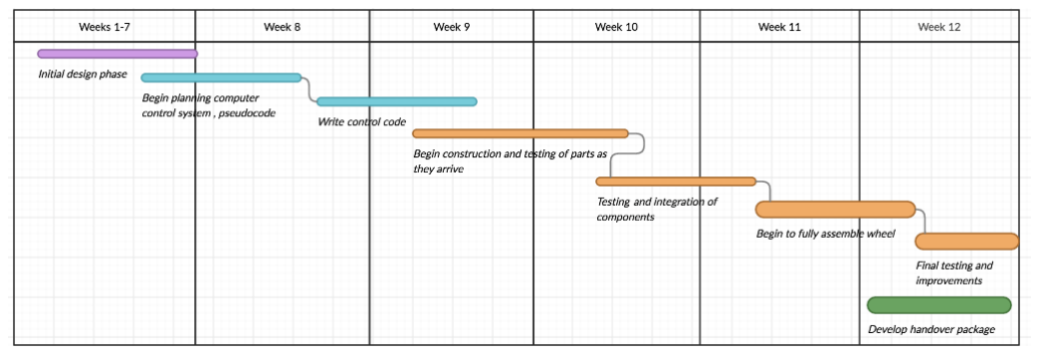
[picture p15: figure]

Figure 6: An outline of the current proposed timeline for the project.

### 5.3 Work Breakdown

Previously, the work has been split into design of the wheel and the design of the rotation mechanism such that these tasks have been divided up on a per person basis and with the occasional collaboration. For future work, the time during the machining of the components and the ordered parts being delivered will require both persons to collaborate on the same part of the project. The tasks which will utilise this collaboration include programming the computer’s speed measurement and stability control of the wheel with the Arduino or by constructing a simulation which reflects the calibration data TorPeDO will generate once the prototype is complete and functional, to assist in verifcation of the prototype’s performance.

## 6 Conclusion

At present, a final design of the first iteration of a Newtonian force calibrator has been produced. The wheel is an echo of the Newtonian force calibrator prototype developed by LIGO as well as an improvement in properties including the use of more appropriately shaped, weighted and interchangeable ‘point-like’ masses. The rotation mechanics will utilise a DC servomotor attached to a timing belt wrapped about the wheel’s axle. The rotation speed will be monitored with a photogate which will produce an error feedback signal to the motor for accurate rotation control. This document also reviewed the client’s requirements, revised the timeline of project goals and discussed the past and future breakdowns of work between group members.

## References

[1] M. Lombardi, “An introduction to frequency calibration - part i,” Cal Lab: International Journal of Metrology, vol. 3, pp. 17–28, Jan. 1996.
[2] D. J. McManus, “Dual torsion pendulum sensor for measurement of terrestrial gravitational forces,” PhD thesis, The Australian National University, Canberra, ACT, Jun. 2019.
[3] D. Estevez, B. Lieunard, F. Marion, B. Mours, L. Rolland, and D. Verkindt, “First tests of a newtonian calibrator on an interferometric gravitational wave detector,” Jun. 2018.
[4] Timesh Mistry and Laurence Datrier and Jeff Kissel and Michael Ross and Colin Weller and Krishna Venkateswara, Ligo h1 ncal prototype results and system review presentation, https://dcc.ligo.org/LIGO-G1901261, 2020.

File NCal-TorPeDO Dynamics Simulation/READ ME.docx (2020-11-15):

Hi there,

This section of the file repository is dedicated to the simulation developed for TorPeDO’s NCal prototype. This simulation was then developed to assist in optimising the prototype’s architecture for TorPeDO’s calibration. The aim of the simulation was to model the setup demonstrated in Figure 1 where m1 and m2 are the slug masses to be used as previously discussed and simulate the two rotating point masses from Figure 5. Mx1, Mx2, My1 and My2 are the masses on TorPeDO’s arms respectively. The right image of Figure 1 provides an overview visual of TorPeDO with Fabry-Perot cavity length d. Located distance L to the right in the same plane is the rotational axis of point masses m1 and m2, following a circular path of radius r with oscillation period T. The simulation was developed in MatLab. When using the simulation, the user inputs values for m1, m2, r, L and T. The most recent version of the simulation (Mark 6) outputs d over three rotation periods of m1 and m2 as demonstrated in Figure 2.

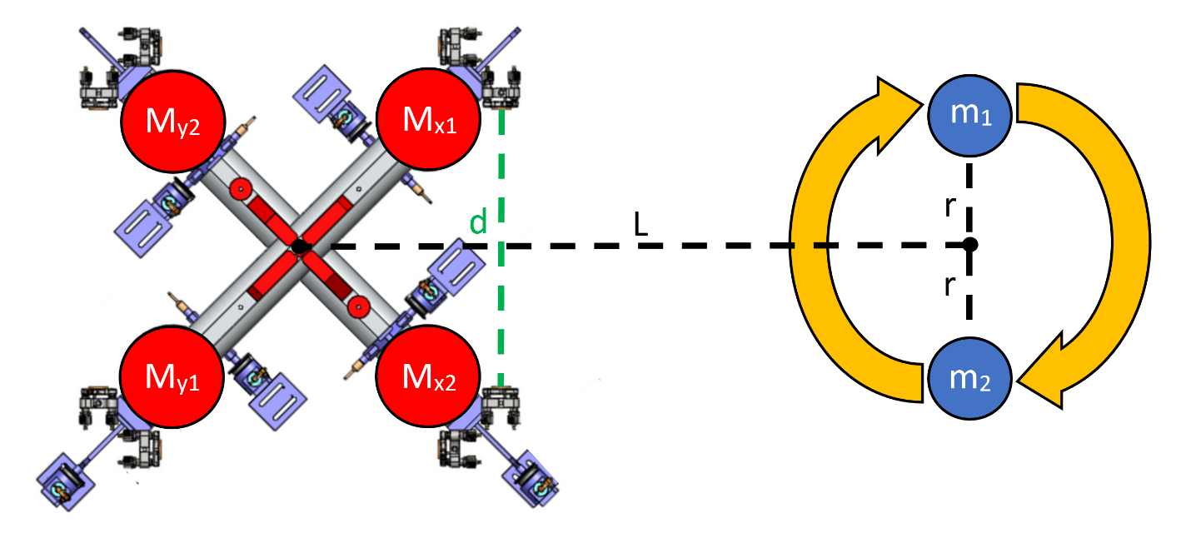
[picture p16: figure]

Figure 1. The setup the simulation is based upon as described above.

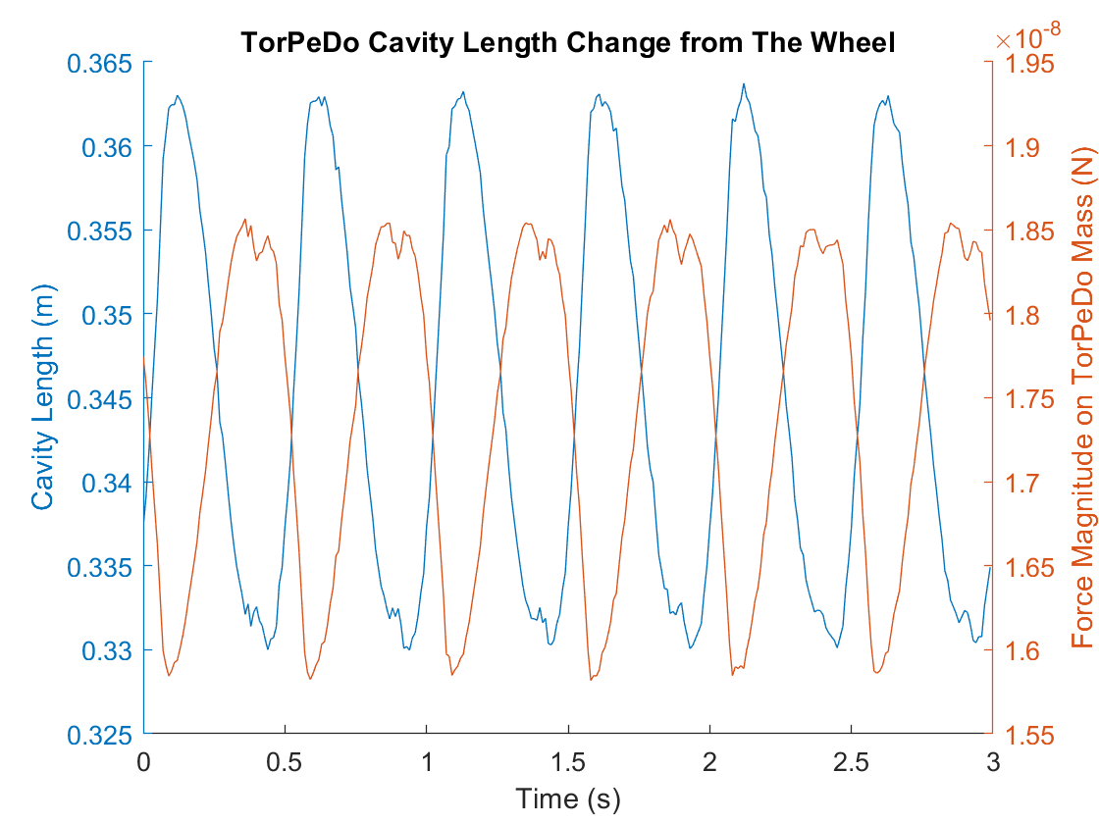
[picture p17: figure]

Figure 2. The output of Mark 6, the cavity length d, plotted alongside the total force magnitude exhibited on Mx1 from Figure 1.

The simulation development took place over six iterations. Mark 1 began as a simplified adaption of Figure 1 and each successive version increased in complexity over the previous. The simulation iterations can be summarised as follows:

Mark 1: (https://thebestportfolio.squarespace.com/s/gravity_sim_MArk1.m) The first simulation was based on the model shown in Figure 3 where the idea was to plot the gravitational signal over a single rotation period of m1 and m2 from a point d away from their circular path. m1 and m2 were made equivalent to a tonne and were 1 meter apart.

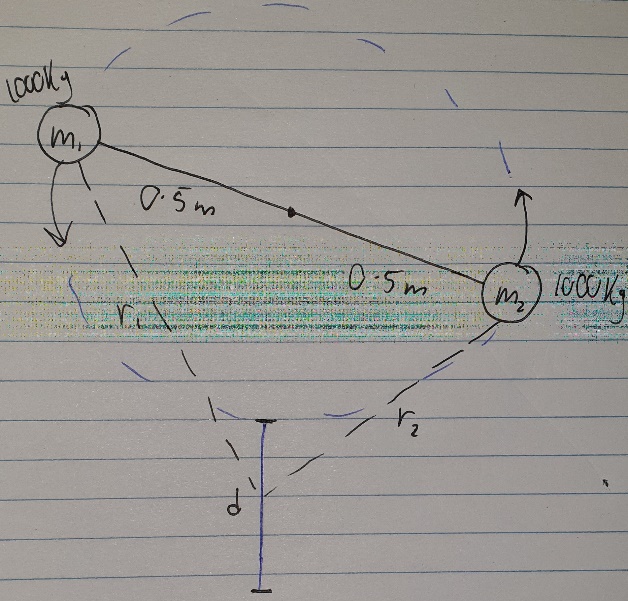
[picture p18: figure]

Figure 3. The model which Mark 1 of the simulation was based upon.

Mark 2: (https://thebestportfolio.squarespace.com/s/gravity_sim_MArk2.m) This version was the same as Mark 1 but allowed the user to set the mass values, their orbiting radii, the maximum distance of the point of analysis and output a surface plot of the gravitational signal as a function of time and along d.

Mark 3: (https://thebestportfolio.squarespace.com/s/gravity_sim_MArk3.m) This version took the basis of the previous iteration and applied it to Mx1 of Figure 9. Mark 3 took in the specific dimensions of TorPeDO (i.e. the arm length, Mx1 and Mx2), allowed the user to set m1, m2, r and L and output the magnitude of gravitational force Mx1 exhibited over a rotation period of the wheel. Note that My1 and My2 were not accounted for as a simplification of the model.

Mark 4: (https://thebestportfolio.squarespace.com/s/gravity_sim_MArk4.m) This version was the same as Mark 3, except the output was d from Figure 9 over three oscillation periods. d was difficult to calculate, requiring approximation methods in MatLab to do so meaning the output was noisy and questionable in accuracy. The problem with the output is that (besides the noise) it is bimodal in frequency and d is changing up to 7cm in length (which is a lot!). However, the plot does follow the same signal of the magnitude of gravitational force on Mx1 which also shouldn’t be bimodal, meaning the analysis of the model used in Figure 1 to generate this simulation is incorrect.

Mark 5: (https://thebestportfolio.squarespace.com/s/gravity_sim_MArk5.m) This version is the same as Mark 4, however is no longer bimodal in its output as the model analysis was readjusted. Here I accounted for My1 and My2 instead of just Mx1 and Mx2. However, extreme changes in d are still present. After much digging through the code I concluded that determining the miniscule values d would realistically take are beyond MatLab’s approximation function capabilities.

Mark 6: (https://thebestportfolio.squarespace.com/s/gravity_sim_MArk6.m) This is the same version as Mark 5, however the output is the rotational acceleration of TorPeDo’s arms (the output the actual device uses).

Note that each MatLab script is accompanied by many comments to explain what each segment of code is doing. This document should be of valuable use also.

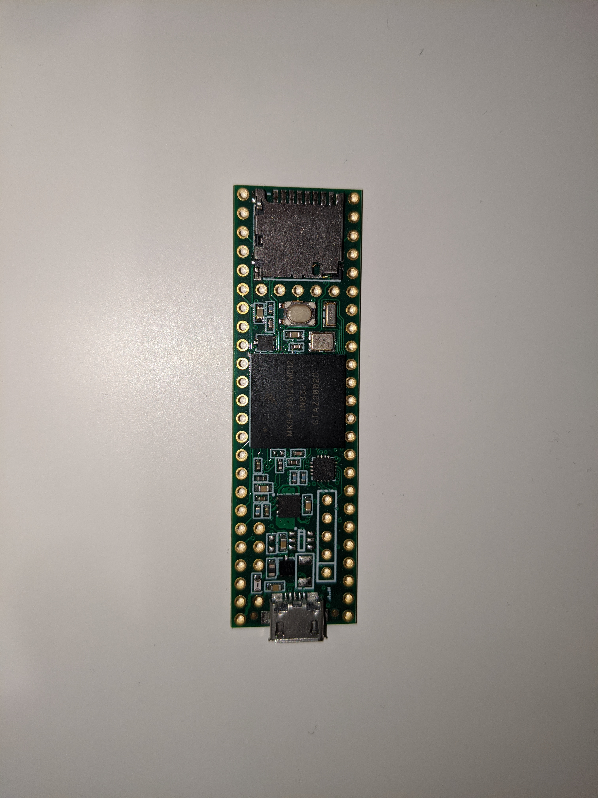
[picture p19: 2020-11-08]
Part Images/Teensy 3.5 (front).jpg

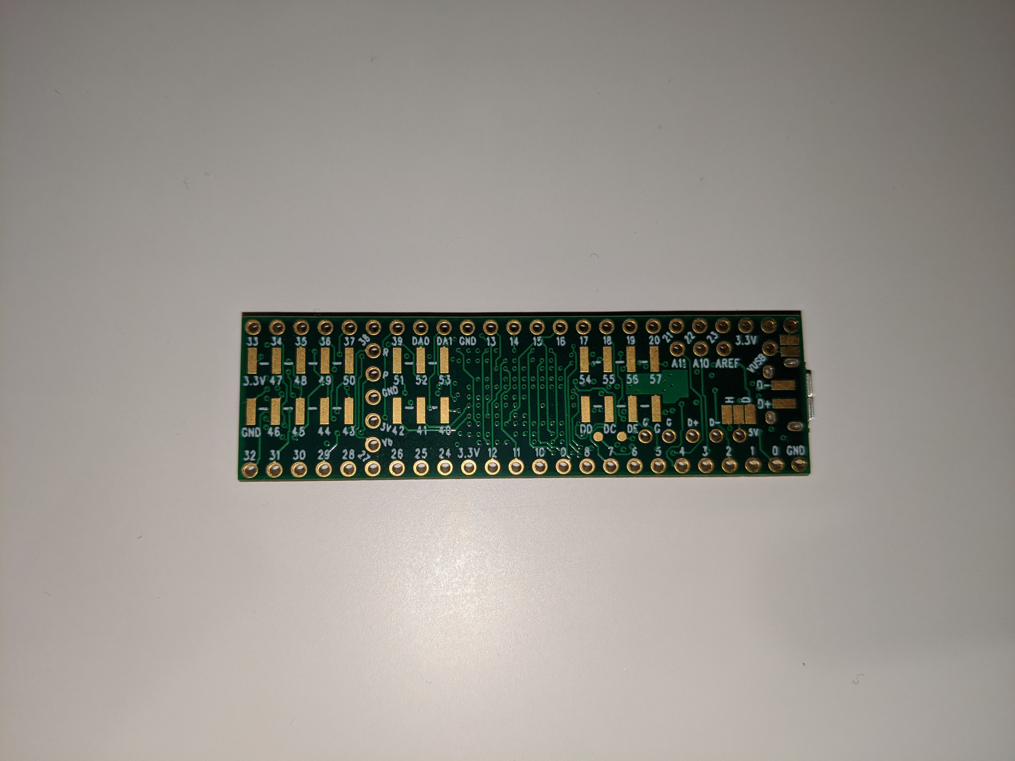
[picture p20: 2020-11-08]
Part Images/Teensy 3.5 (back).jpg

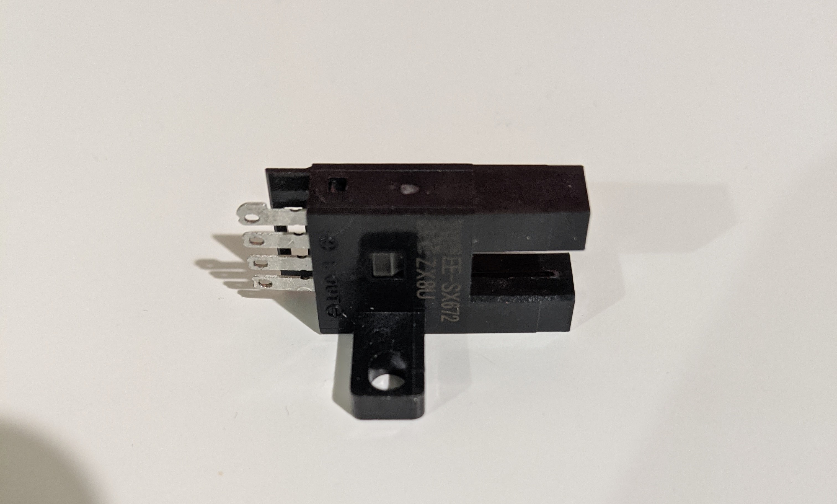
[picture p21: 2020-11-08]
Part Images/Photogate.jpg

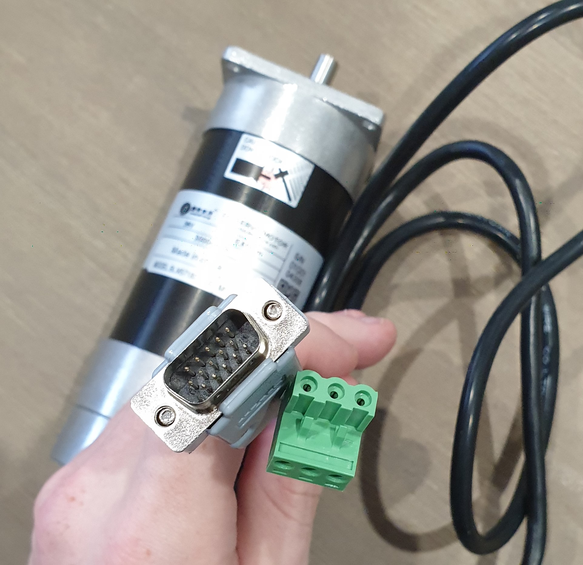
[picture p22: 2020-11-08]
Part Images/Servo Motor_3.jpg

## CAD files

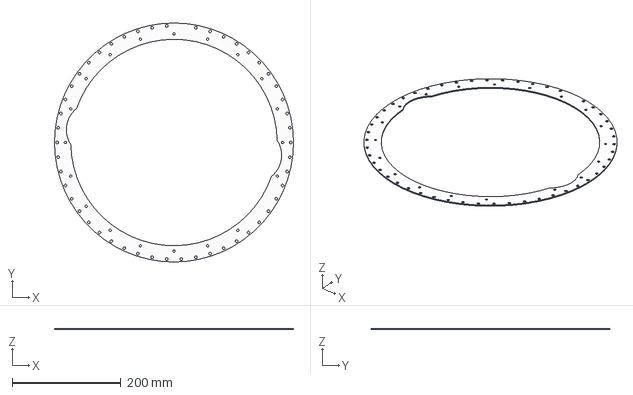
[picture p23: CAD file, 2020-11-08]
Individual Component STEP Files/chopper_wheel.step
440.0 x 440.0 x 2.00 mm

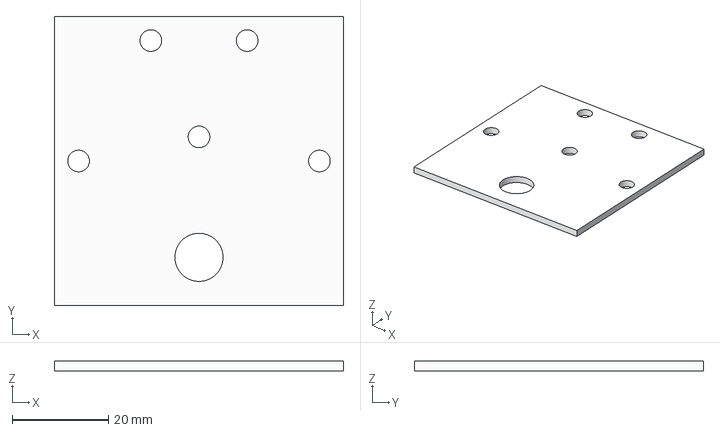
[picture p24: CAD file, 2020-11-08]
Individual Component STEP Files/light_gate_lid.step
60.0 x 60.0 x 2.00 mm

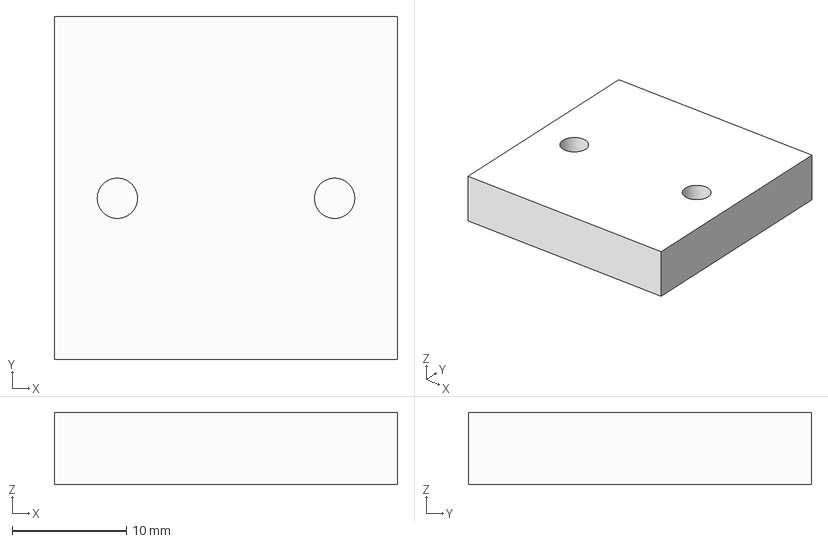
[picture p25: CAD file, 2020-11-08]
Individual Component STEP Files/light_gate_spacer_plate.step
30.0 x 30.0 x 6.30 mm

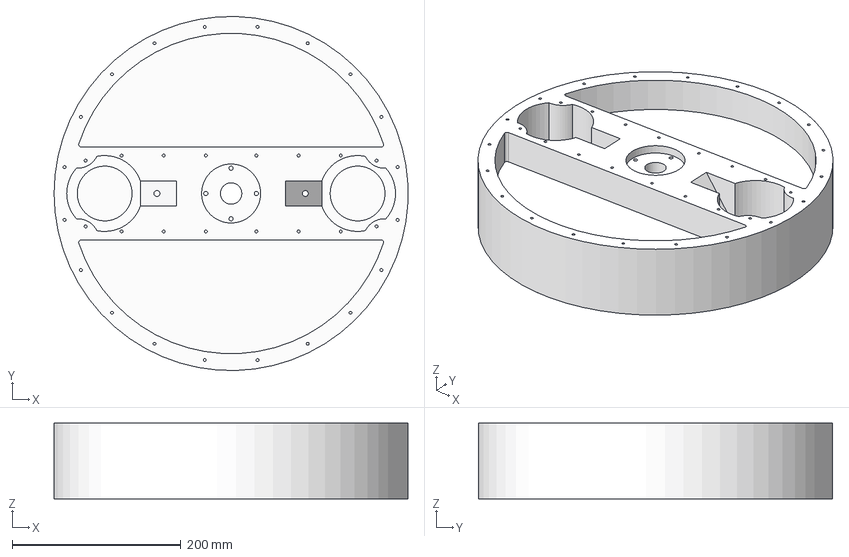
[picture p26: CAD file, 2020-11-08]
Individual Component STEP Files/wheel_body.step
419.7 x 419.9 x 90.0 mm

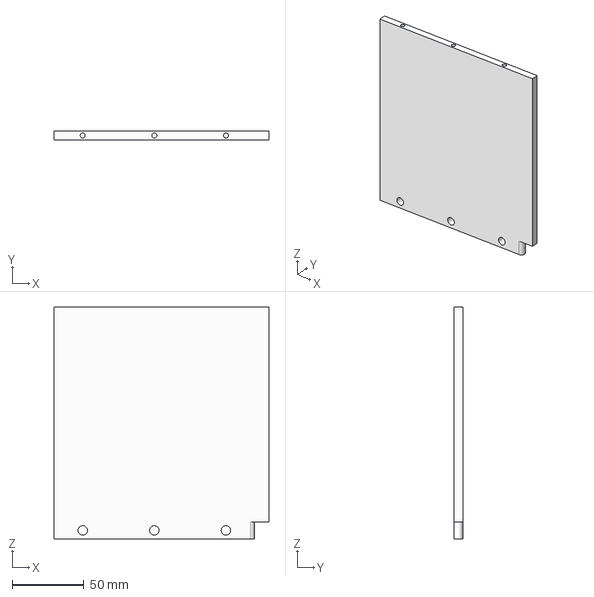
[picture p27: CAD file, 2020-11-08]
Individual Component STEP Files/side_cover_side_wall.step
150.0 x 6.00 x 162.0 mm

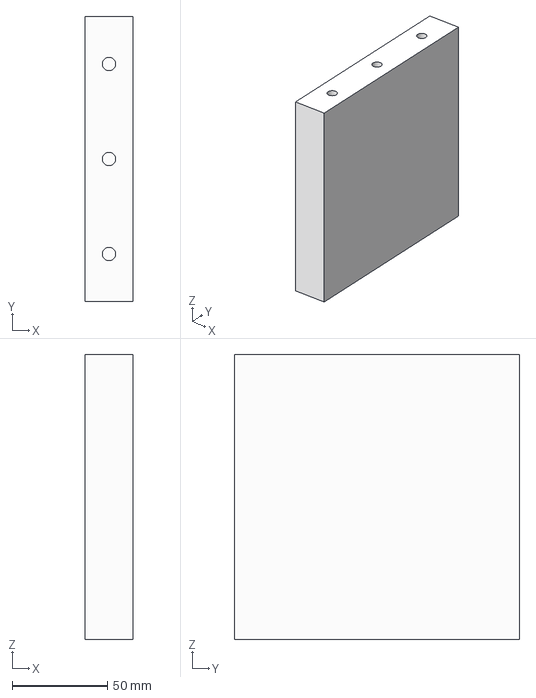
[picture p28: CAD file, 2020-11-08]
Individual Component STEP Files/securing_structure_wall.step
25.0 x 150.0 x 150.0 mm

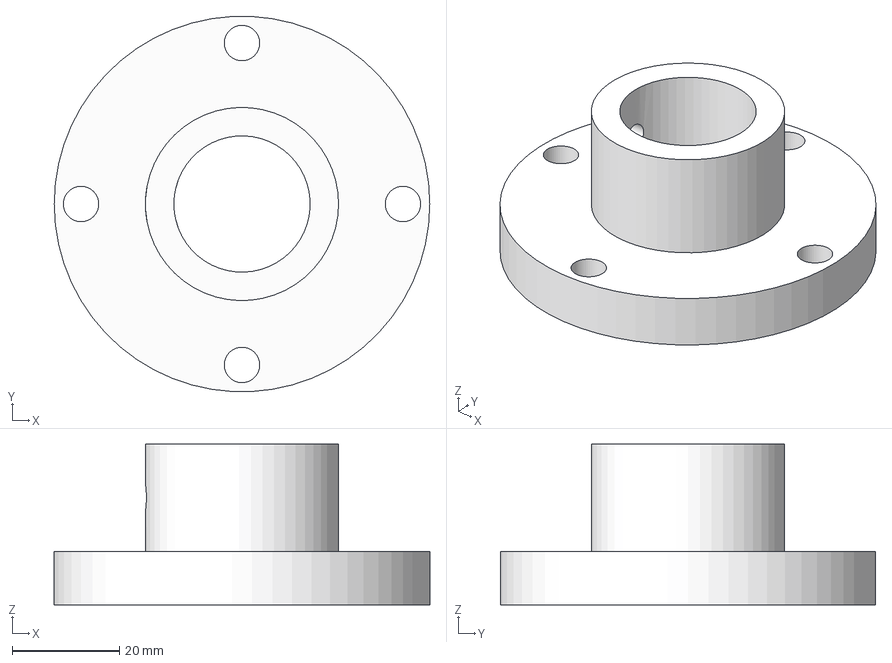
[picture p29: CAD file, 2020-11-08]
Individual Component STEP Files/axel_holder.step
70.0 x 69.9 x 30.0 mm

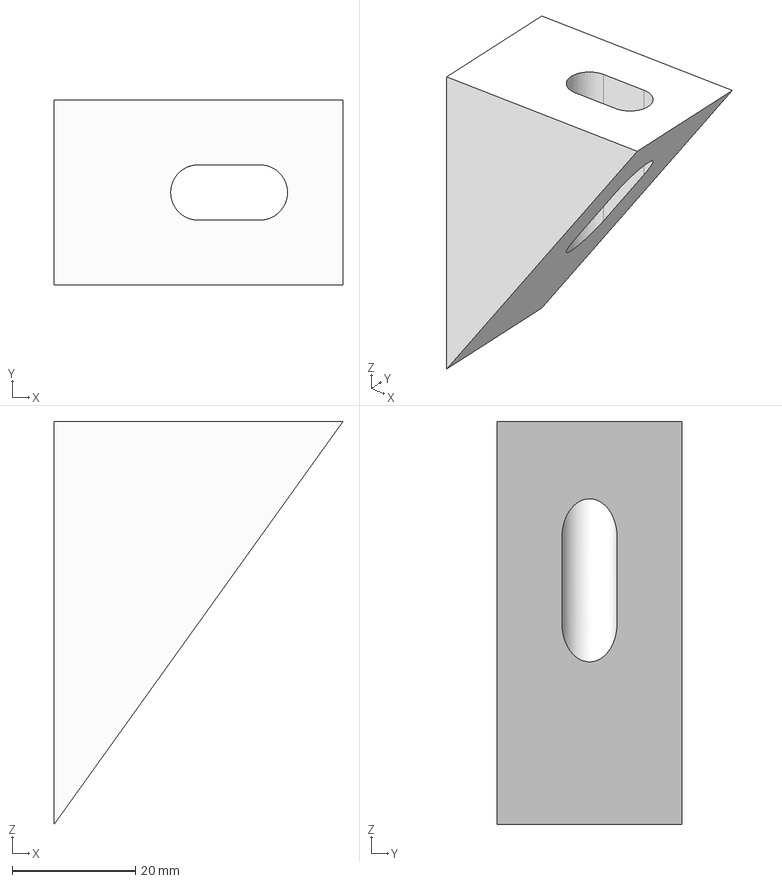
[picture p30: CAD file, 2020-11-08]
Individual Component STEP Files/weight_holders.step
47.0 x 30.0 x 65.5 mm

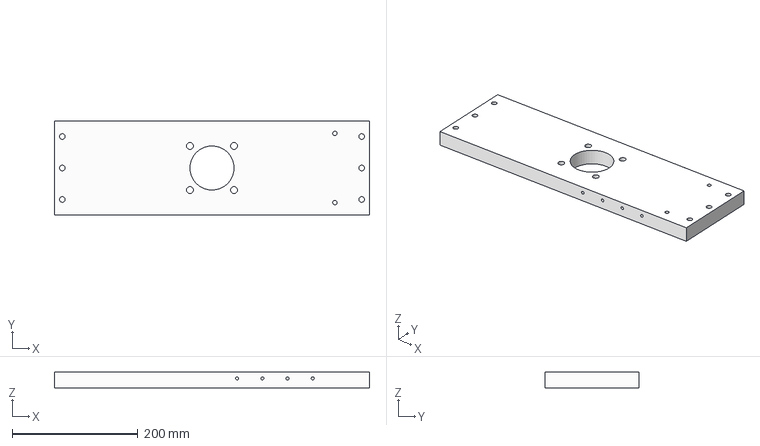
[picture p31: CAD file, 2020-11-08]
Individual Component STEP Files/securing_structure_lid.step
500.5 x 150.0 x 25.0 mm

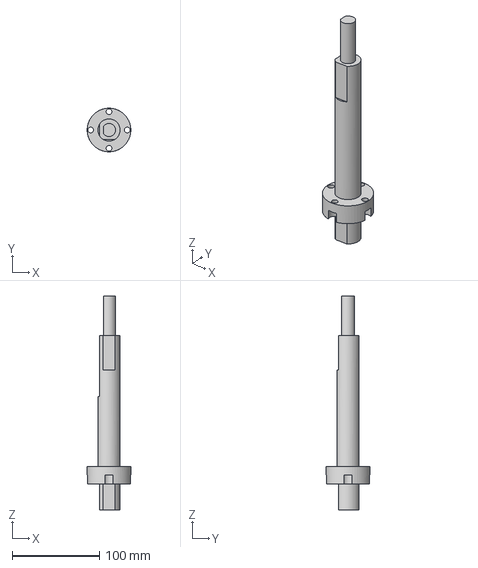
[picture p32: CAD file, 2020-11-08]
Individual Component STEP Files/axle.step
50.0 x 50.0 x 245.0 mm

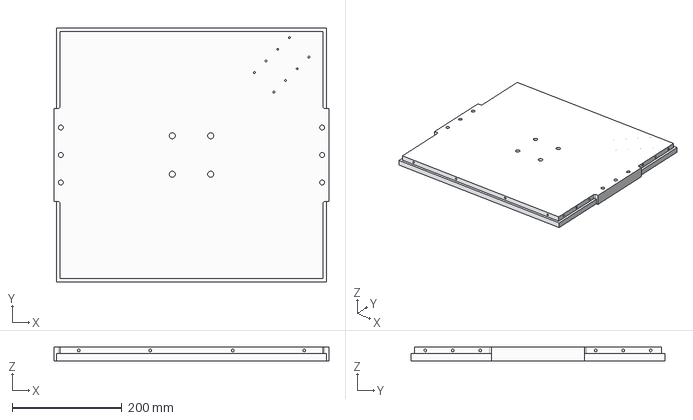
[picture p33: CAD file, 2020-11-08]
Individual Component STEP Files/base_plate.step
500.5 x 462.0 x 25.0 mm

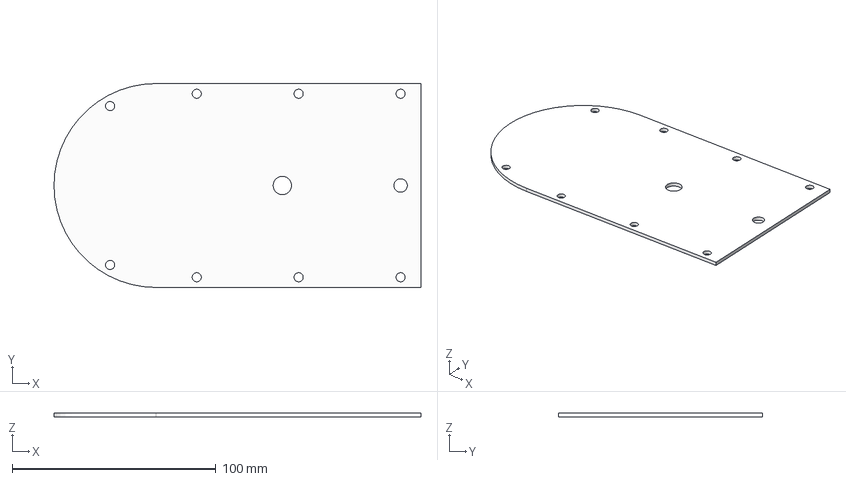
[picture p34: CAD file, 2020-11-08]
Individual Component STEP Files/weight_lids.step
180.0 x 100.0 x 2.00 mm

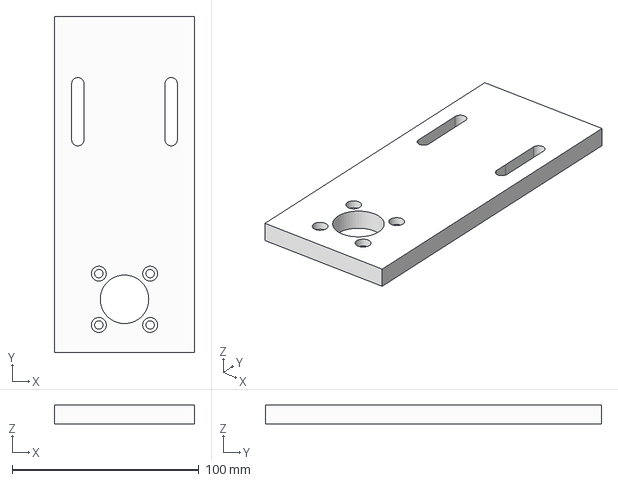
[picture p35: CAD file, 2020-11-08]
Individual Component STEP Files/motor_mount.step
75.0 x 180.0 x 10.0 mm

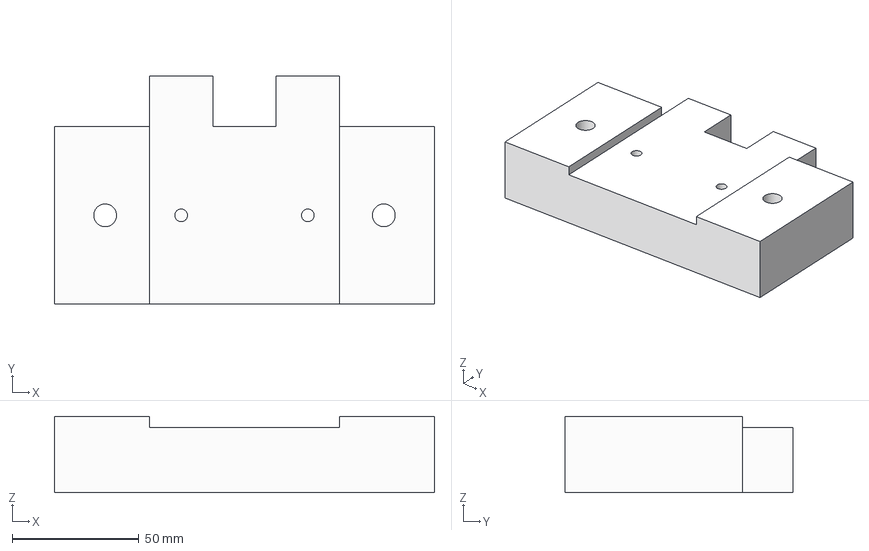
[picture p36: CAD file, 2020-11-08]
Individual Component STEP Files/motor_mount_spacer_plate.step
150.0 x 90.0 x 30.0 mm

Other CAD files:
Individual Component STEP Files/weights.step
Individual Component STEP Files/side_cover_front_wall.step
Individual Component STEP Files/light_gate_lid_holder.step
Individual Component STEP Files/sid_cover_lid_light_gate.step
Fusion360 CAD Files/axel_holder v23.f3d
Fusion360 CAD Files/axle v77.f3d
Fusion360 CAD Files/base_plate v90.f3d
Fusion360 CAD Files/chopper_wheel v9.f3d
Fusion360 CAD Files/feet v2.f3d
Fusion360 CAD Files/flange_bearing v6.f3d
Fusion360 CAD Files/light_gate v4.f3d
Fusion360 CAD Files/light_gate_holder v5.f3d
Fusion360 CAD Files/motor v11.f3d
Fusion360 CAD Files/motor_mount v104.f3d
Fusion360 CAD Files/motor_mount_spacer_plate v51.f3d
Fusion360 CAD Files/securing_structure_lid v106.f3d
Fusion360 CAD Files/securing_structure_wall v15.f3d
Fusion360 CAD Files/side_cover_front_wall v40.f3d
Fusion360 CAD Files/side_cover_lid v28.f3d
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

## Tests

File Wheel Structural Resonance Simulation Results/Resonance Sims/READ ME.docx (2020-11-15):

Hi there,

This section of the file repository is dedicated to the resonance simulation results for different NCal prototype designs, generated using Fusion360 to confirming the best implementation of a lid mechanism to the wheel. The client (Bram) noted that he wanted to add lids to the device to assist in reducing modes in the wheel’s structure as it rotates. This was a great design idea and required the simulating of several lid implementations to confirm which was best for reducing the modal frequency. Fusion360 was used to simulate these mechanics, where the top and bottom of the axel were fixed in place and the only forces applied to the wheel were those of gravity and a rotational velocity of 360 deg/s (1 total rotation every second). The simulation process took some time as research and practice behind the simulation mechanics were required.

Five different lid implementation designs were analysed and the results are reflected in the following table. Note that lids were also added above the masses when the center filling versions of the wheel underwent were simulation, as these lids would be implemented to assist in holding the masses in place.

Lid/Infill Application | Lid Thickness (mm) | Lowest Rotational Mode Frequency (Hz) | Fusion 360 Model

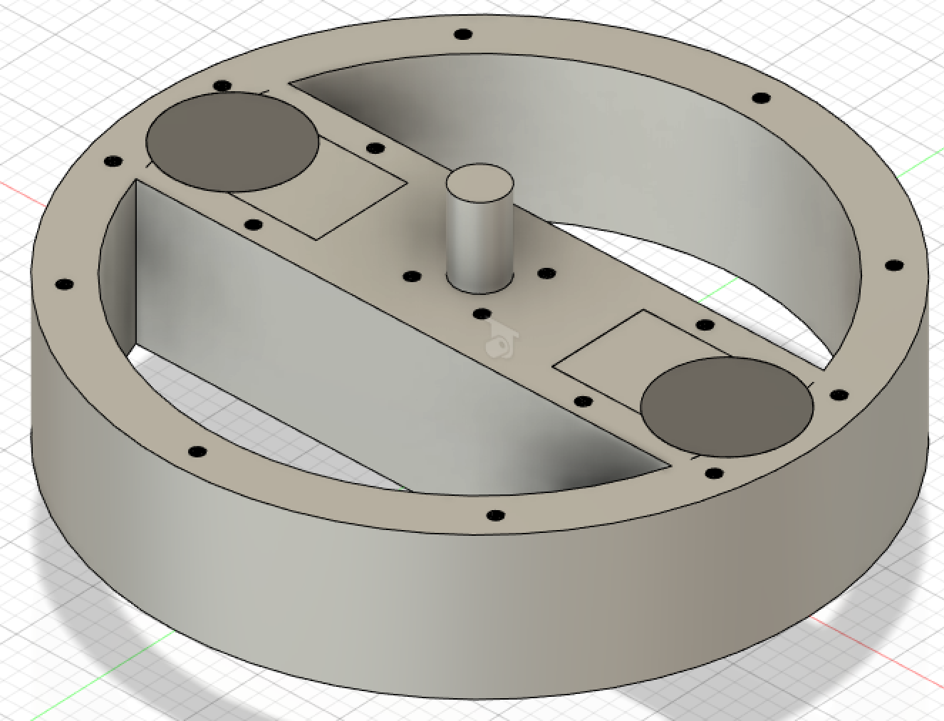
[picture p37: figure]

None | 0 | 162.1

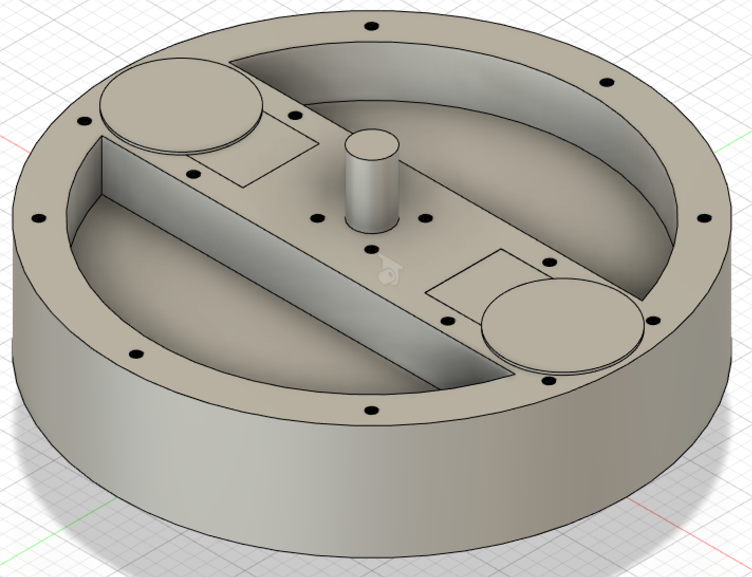
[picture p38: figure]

Center | 10 | 132.0

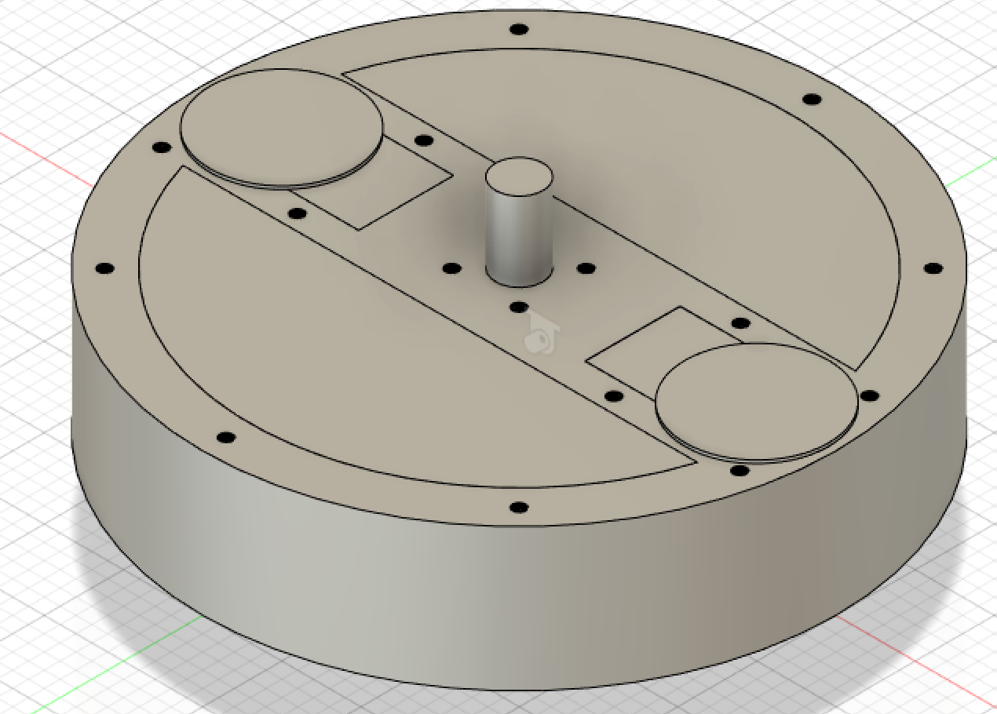
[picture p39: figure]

Filled in Center | 45 | 117.6

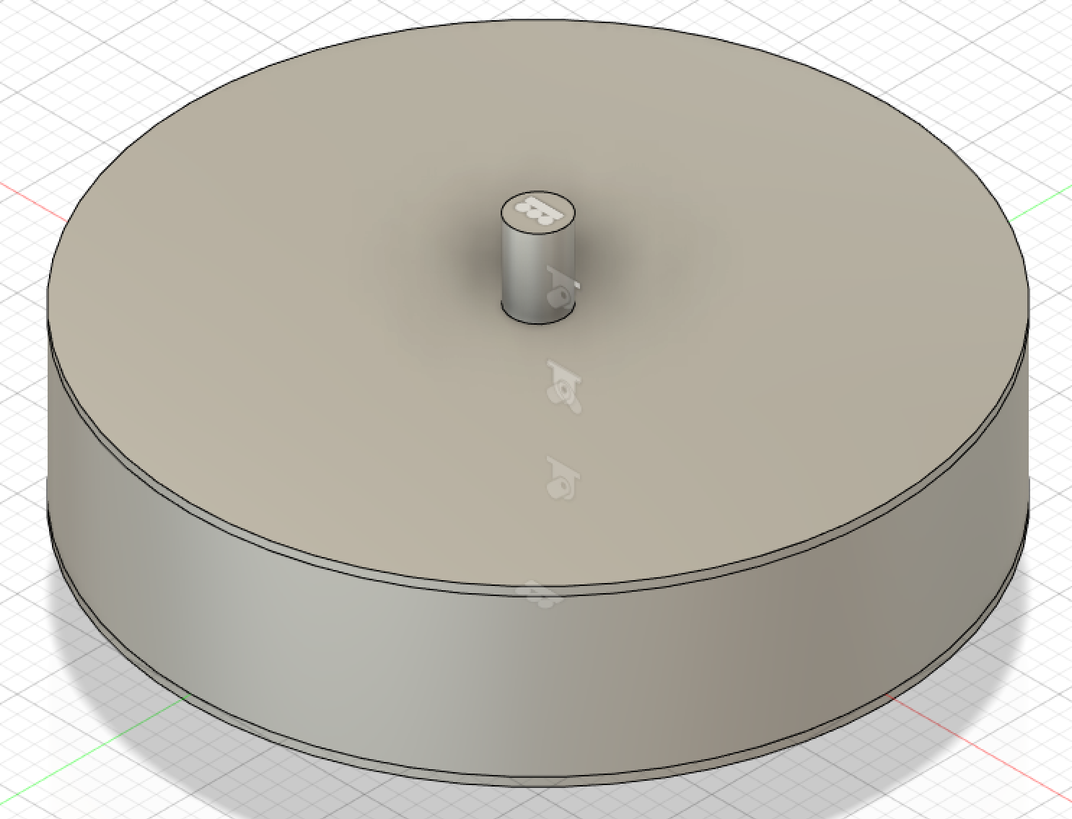
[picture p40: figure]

Top and Bottom | 5 | 61.1

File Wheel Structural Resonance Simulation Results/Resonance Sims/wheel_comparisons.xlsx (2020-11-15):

Lid Application | Rotational Mode Frequency (Hz)
None | 132
Center | 162.1
Filled in Center | 117.6
Top and Bottom | 61.13

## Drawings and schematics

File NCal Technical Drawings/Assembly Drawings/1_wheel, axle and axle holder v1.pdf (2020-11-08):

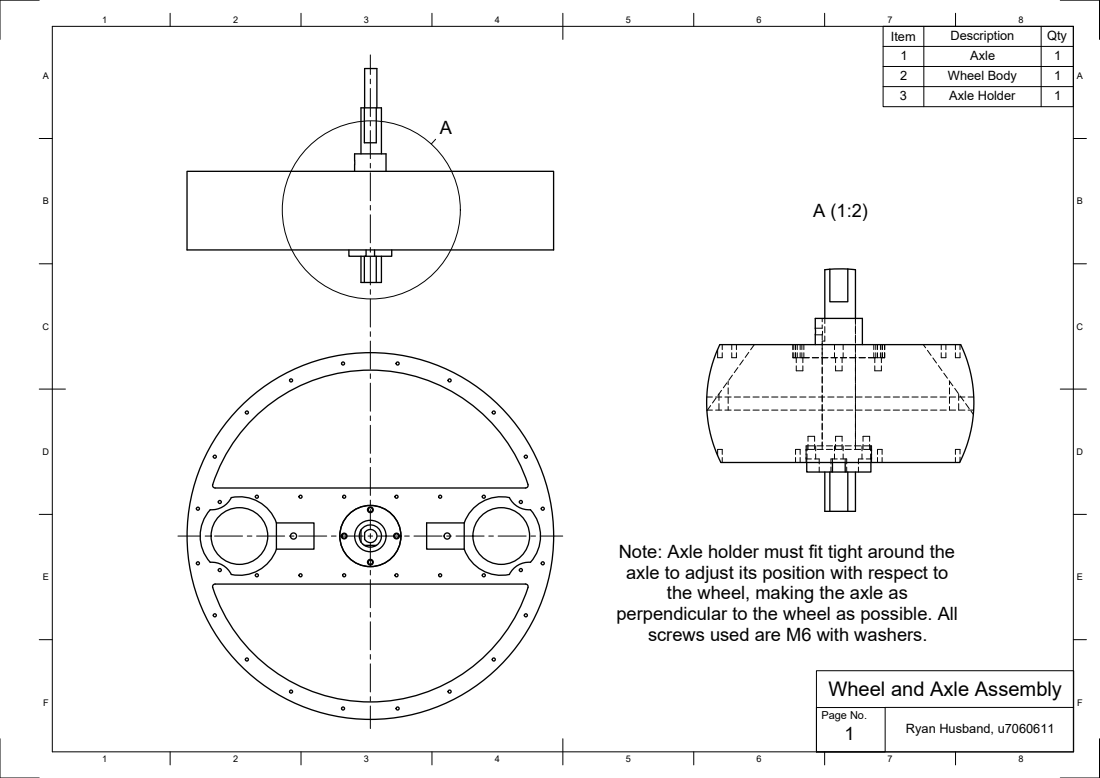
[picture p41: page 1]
Ryan Husband, u7060611; Page No.

Item | Description | Qty
1 | Axle | 1
2 | Wheel Body | 1
3 | Axle Holder | 1

Note: Axle holder must fit tight around the
axle to adjust its position with respect to
the wheel, making the axle as
perpendicular to the wheel as possible. All
screws used are M6 with washers.

F Wheel and Axle Assembly

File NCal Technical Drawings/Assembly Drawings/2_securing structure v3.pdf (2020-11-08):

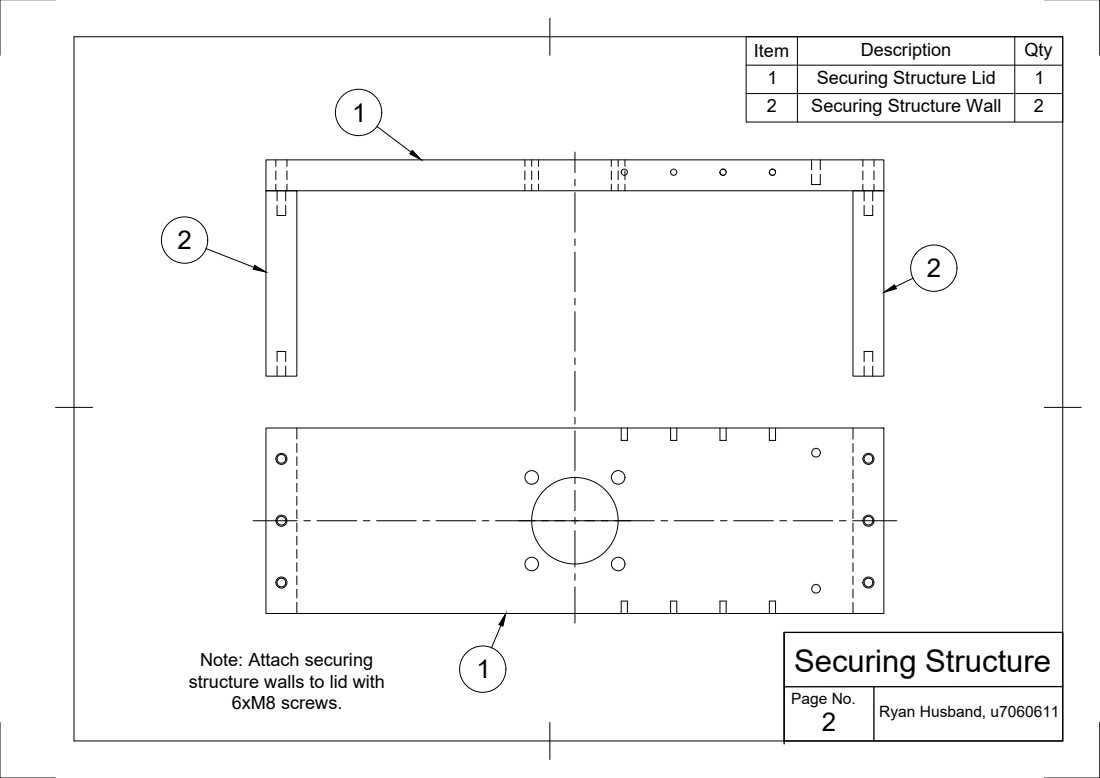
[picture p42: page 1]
Securing Structure

Item | Description | Qty
1 | Securing Structure Lid | 1
2 | Securing Structure Wall | 2

Note: Attach securing
structure walls to lid with
6xM8 screws.

Ryan Husband, u7060611 Page No.

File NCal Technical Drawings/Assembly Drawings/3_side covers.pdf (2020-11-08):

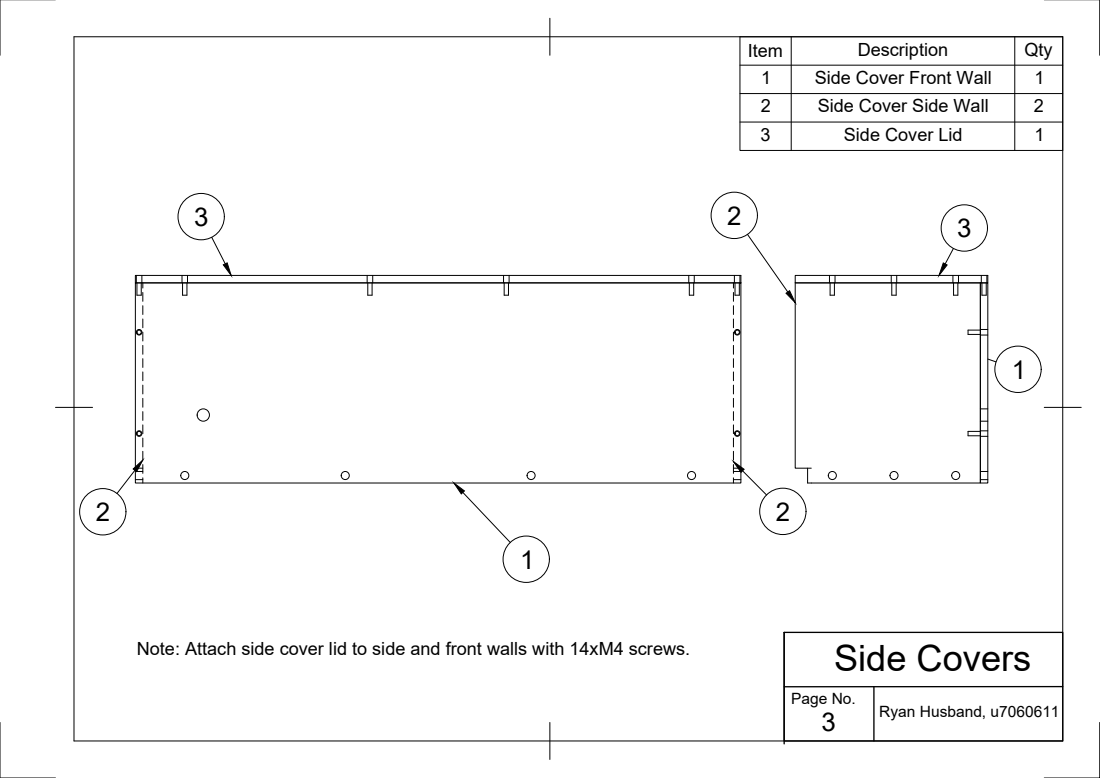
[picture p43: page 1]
Side Covers

Item | Description | Qty
1 | Side Cover Front Wall | 1
2 | Side Cover Side Wall | 2
3 | Side Cover Lid | 1

Note: Attach side cover lid to side and front walls with 14xM4 screws.

Ryan Husband, u7060611 Page No.

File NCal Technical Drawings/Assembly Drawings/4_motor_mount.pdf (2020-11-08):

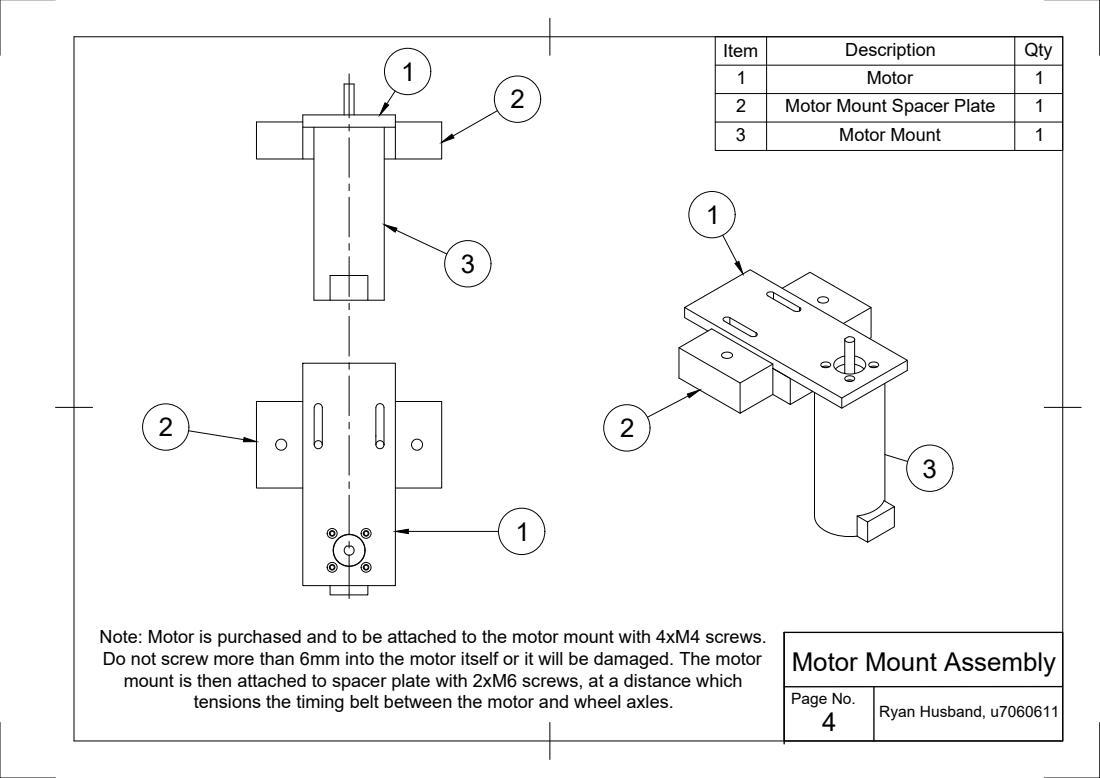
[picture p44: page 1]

Item | Description | Qty
1 | Motor | 1
2 | Motor Mount Spacer Plate | 1
3 | Motor Mount | 1

Note: Motor is purchased and to be attached to the motor mount with 4xM4 screws.
Do not screw more than 6mm into the motor itself or it will be damaged. The motor
mount is then attached to spacer plate with 2xM6 screws, at a distance which

Motor Mount Assembly

tensions the timing belt between the motor and wheel axles.

Ryan Husband, u7060611 Page No.

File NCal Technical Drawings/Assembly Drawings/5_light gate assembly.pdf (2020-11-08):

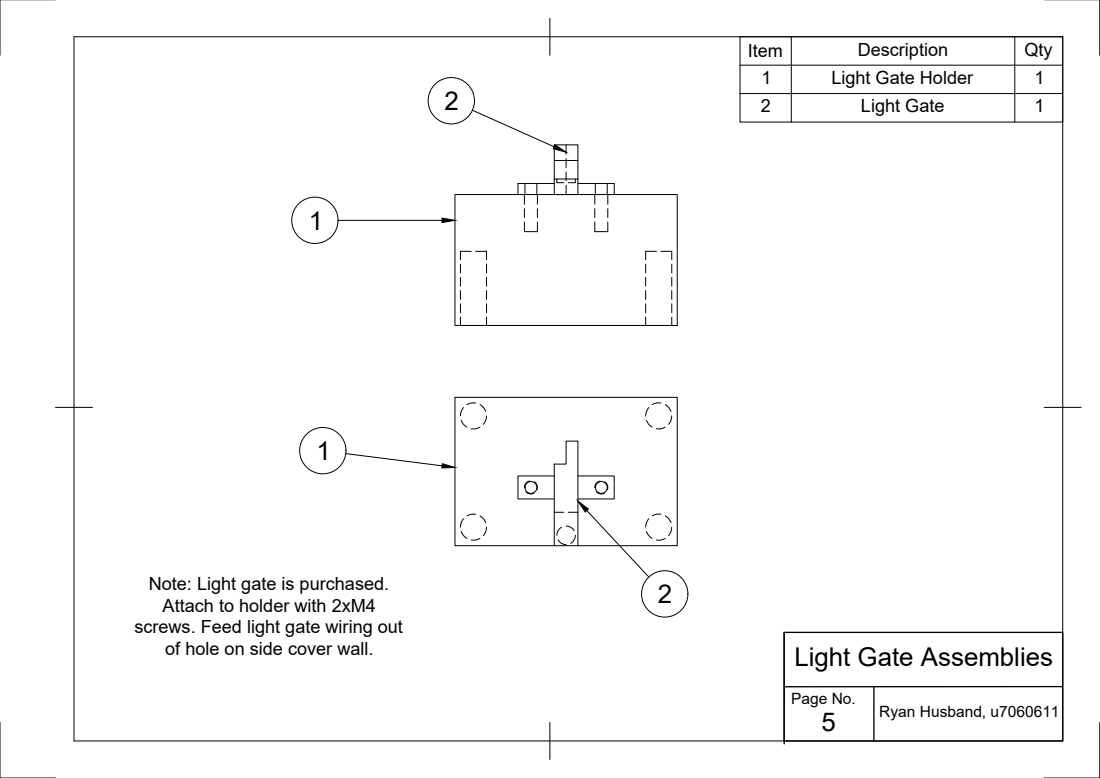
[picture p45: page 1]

Item | Description | Qty
1 | Light Gate Holder | 1
2 | Light Gate | 1

Note: Light gate is purchased.
Attach to holder with 2xM4
screws. Feed light gate wiring out
of hole on side cover wall.

Light Gate Assemblies

Ryan Husband, u7060611 Page No.

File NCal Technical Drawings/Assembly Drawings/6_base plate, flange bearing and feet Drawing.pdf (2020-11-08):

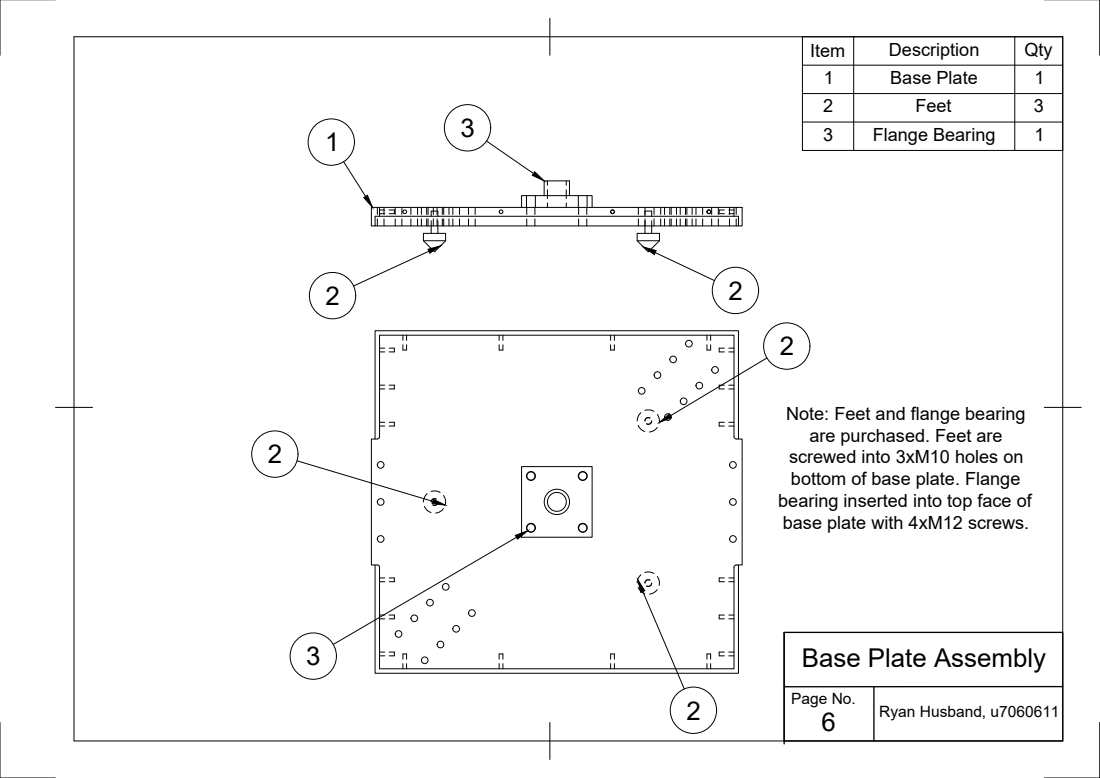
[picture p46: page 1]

Item | Description | Qty
1 | Base Plate | 1
2 | Feet | 3
3 | Flange Bearing | 1

Note: Feet and flange bearing
are purchased. Feet are
screwed into 3xM10 holes on
bottom of base plate. Flange
bearing inserted into top face of
base plate with 4xM12 screws.

Base Plate Assembly

Ryan Husband, u7060611 Page No.

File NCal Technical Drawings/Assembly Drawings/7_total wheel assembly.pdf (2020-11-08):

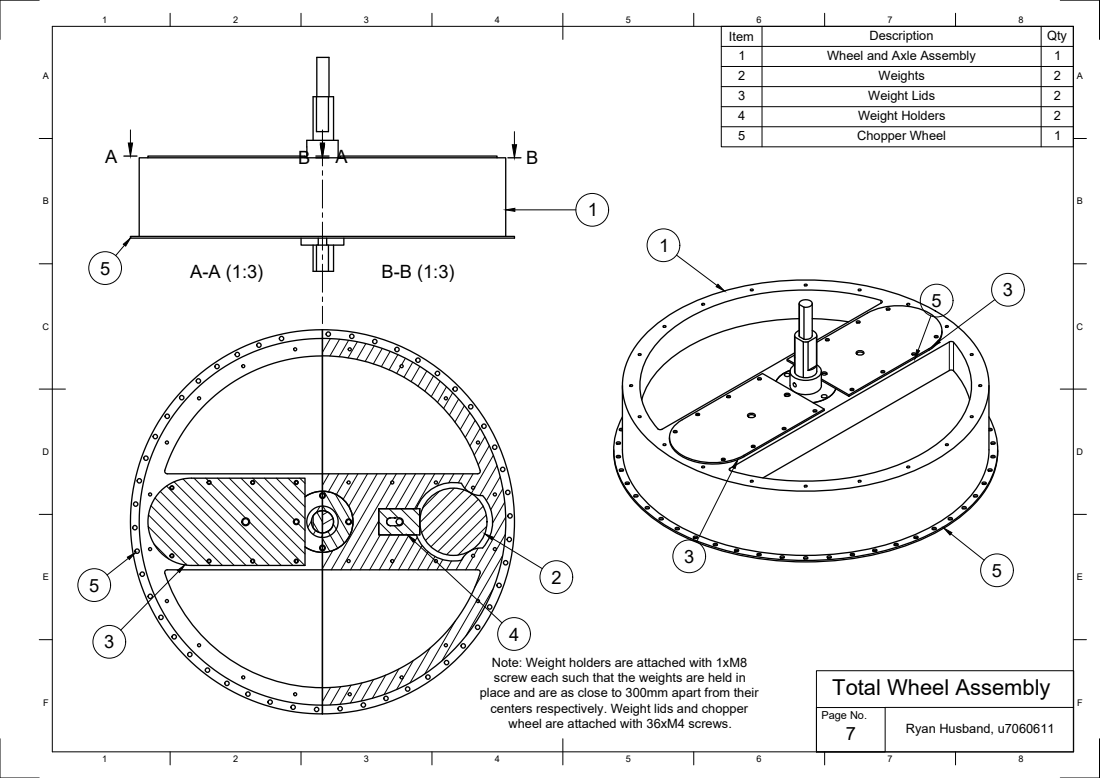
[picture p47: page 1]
Ryan Husband, u7060611; Page No.

Item | Description | Qty
1 | Wheel and Axle Assembly | 1
2 | Weights | 2
3 | Weight Lids | 2
4 | Weight Holders | 2
5 | Chopper Wheel | 1

Note: Weight holders are attached with 1xM8
screw each such that the weights are held in
place and are as close to 300mm apart from their
centers respectively. Weight lids and chopper
wheel are attached with 36xM4 screws.

F Total Wheel Assembly

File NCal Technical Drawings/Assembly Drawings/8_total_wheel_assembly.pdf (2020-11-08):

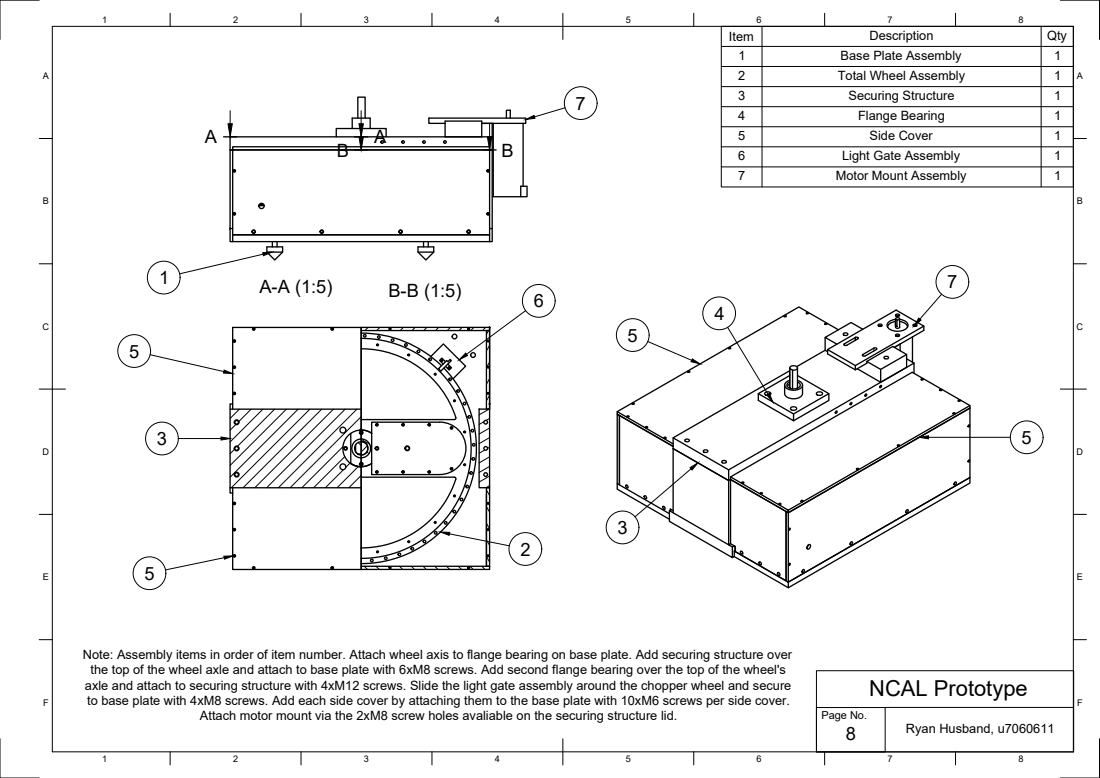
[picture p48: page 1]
F NCAL Prototype; Ryan Husband, u7060611; Page No.

Item | Description | Qty
1 | Base Plate Assembly | 1
2 | Total Wheel Assembly | 1
3 | Securing Structure | 1
4 | Flange Bearing | 1
5 | Side Cover | 1
6 | Light Gate Assembly | 1
7 | Motor Mount Assembly | 1

Note: Assembly items in order of item number. Attach wheel axis to flange bearing on base plate. Add securing structure over
the top of the wheel axle and attach to base plate with 6xM8 screws. Add second flange bearing over the top of the wheel's
axle and attach to securing structure with 4xM12 screws. Slide the light gate assembly around the chopper wheel and secure
to base plate with 4xM8 screws. Add each side cover by attaching them to the base plate with 10xM6 screws per side cover.

Attach motor mount via the 2xM8 screw holes avaliable on the securing structure lid.

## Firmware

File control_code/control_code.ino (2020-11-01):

// NCal control code
// PHYS6701 S2 2020
// Monique Cockram and Ryan Husband


/*<Code stolen from <https://github.com/sparkfun/Photo_Interrupter_Breakout> 
 * used on https://www.youtube.com/watch?v=jNMb2Az-hIY&ab_channel=SparkFunElectronics
  Simple Sketch for getting started with Photo Interrupter Breakout */

//Declare libraries
#include <SoftwareSerial.h>

//set pins for the motor and photogate
const int gatePin = 10;
int val;


int BPin = 6; //backwards motor in1
int FPin = 7; //forwards motor in2

int speedPin = 21; //enA 



float chosen_period = 0.7; //time in seconds for one rotation


float period; //the period of rotation of the wheel
float num_holes = 2; //the number of holes around the circumference of the wheel
unsigned long prev_time = 0;
unsigned long current_time = 0;
float time_taken = 0;
int speed_val;


void setup() {
  // put your setup code here, to run once:

  Serial.begin(9600);
  

//initialise pins

  pinMode(13, OUTPUT);
  pinMode(gatePin, INPUT);


  pinMode(BPin, OUTPUT);
  pinMode(FPin, OUTPUT);
  pinMode(speedPin, OUTPUT);
  

  attachInterrupt(digitalPinToInterrupt(gatePin), timing_function, RISING);


  digitalWrite(BPin,LOW);
  digitalWrite(FPin,HIGH);
  speed_val = 100; //an initial speed value
  analogWrite(speedPin, speed_val); //previous projects showed that this is lowest speed to overcome friction


}


void timing_function() {
  //interupt function to execute when the photogate changes to HIGH
  current_time = millis();
  time_taken = current_time - prev_time;
  prev_time = current_time;
  if ((period > chosen_period) && (speed_val < 255)) {
    speed_val = speed_val + 1; //increasing speed_val if too slow
    analogWrite(speedPin, speed_val);
    }
    
  if ((period < chosen_period) && (speed_val > 40)) {
    speed_val = speed_val - 1;
    analogWrite(speedPin, speed_val);
    }
  }




void loop() {
  // put your main code here, to run repeatedly:
 
   //Read photogate data
  val = digitalRead(gatePin);
  //Print photogate data in binary
  //Serial.print(val); //printing photogate data
  //Serial.print("\n");

  //If photogate detects something, turn Teensy LED on
  if (val == HIGH) {
    digitalWrite(LED_BUILTIN, HIGH);
  }

  //Leave LED off otherwise
  else
  {
    digitalWrite(LED_BUILTIN, LOW);
  }

  Serial.print(time_taken);
  Serial.print("___");
  period = time_taken*num_holes/1000; //in seconds
  Serial.print(period);
  Serial.print("___");
  delay(10); 
  Serial.print(speed_val);
  Serial.print("\n");
  
}

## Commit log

2020-10-07 motor added maybe
2020-10-28 started adding motor code
2020-10-29 first attempt at motor code added
